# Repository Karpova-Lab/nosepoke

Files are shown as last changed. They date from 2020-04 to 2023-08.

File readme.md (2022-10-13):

# Nosepoke
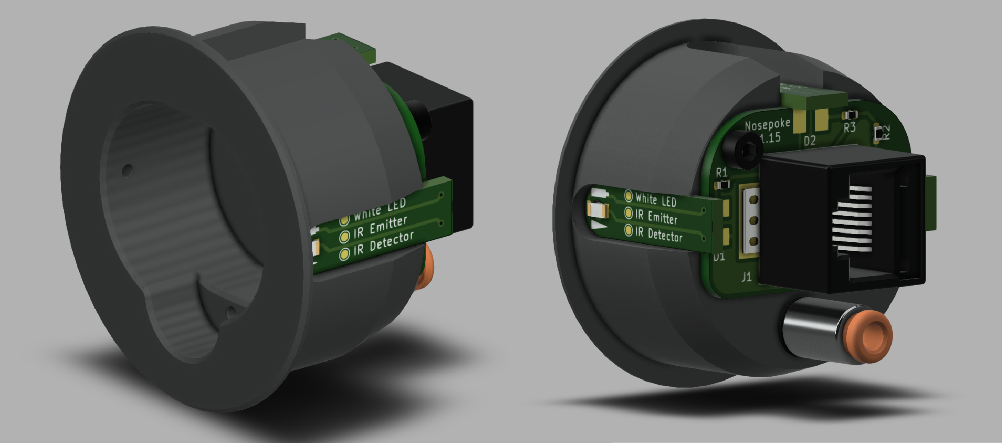
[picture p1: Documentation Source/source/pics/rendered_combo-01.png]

Full Documentation here: [https://karpova-lab.github.io/nosepoke/](https://karpova-lab.github.io/nosepoke/)

Ask questions here: [https://github.com/Karpova-Lab/nosepoke/discussions](https://github.com/Karpova-Lab/nosepoke/discussions)

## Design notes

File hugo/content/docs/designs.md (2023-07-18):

---
title: BOM and Design files
weight: 1
prev_txt: Overview
prev_link: ..
next_txt: Building
next_link: building
---

# Bill of Materials and Design Files

{{< pic file="parts.jpg" >}}

## Plastic Nosepoke Body

{{< columns >}}
{{< pic file="plastic.png" >}}
<--->

{{< pic file="nosepoke.png" >}}
{{< /columns >}}

{{< download filename="nosepoke.stl" text="nosepoke.stl" >}}
<br>
{{< download filename="nosepoke.step" text="nosepoke.step" >}}
<br>
{{< download filename="nosepoke_drawing.pdf" text="nosepoke_drawing.pdf" >}}

## PCBs and Electronics

PCB source files are on [GitHub](https://github.com/Karpova-Lab/nosepoke/tree/master/pcb)

{{< columns >}}

{{< pic file="back_pcb.png" >}}
{{< caption text="Rear PCB" >}}

<div style="text-align:center;">
<a href="https://oshpark.com/shared_projects/07c1qRaL">Order from OSH Park </a>
</div>
<--->

{{< pic file="outer_pcb.png" >}}

{{< caption text="Perimeter PCB" >}}

<div style="text-align:center;">
<a href="https://oshpark.com/shared_projects/ehOwH3Wp">Order from OSH Park </a>
</div>

{{< /columns >}}

| Qty | Reference | Description        | Value/MPN                                                                                                                                          |
| --- | --------- | ------------------ | -------------------------------------------------------------------------------------------------------------------------------------------------- |
| 1   | D1        | IR LED             | [IR26-21C/L110/TR8](https://www.digikey.com/products/en?keywords=1080-1357-1-ND)                                                                   |
| 1   | D2        | Diffused White LED | [23-11/T7D-CQ2R2QY/2A](https://www.digikey.com/products/en?keywords=1080-1593-1-ND)                                                                |
| 1   | J1        | RJ45 Jack          | [0855135013](https://www.digikey.com/products/en?keywords=WM3553CT-ND)                                                                             |
| 1   | Q1        | Phototransistor    | [PT26-21C/TR8](https://www.digikey.com/products/en?keywords=1080-1386-1-ND)                                                                        |
| 1   | R1        | 0603 Resistor      | [200Ω](https://www.digikey.com/en/products/detail/panasonic-electronic-components/ERJ-3EKF2000V/196205?s=N4IgTCBcDaIKICUBSBaAzHA0gMTABgIDUQBdAXyA) |
| 1   | R2        | 0603 Resistor      | [82Ω](https://www.digikey.com/products/en?keywords=311-82.0HRCT-ND)                                                                                |
| 1   | R3        | 0603 Resistor      | [10KΩ](https://www.digikey.com/en/products/detail/yageo/RC0603JR-0710KL/726700)                                                                    |
| 1   | R4        | 0603 Resistor      | [20KΩ](https://www.digikey.com/en/products/detail/yageo/RC0603JR-0720KL/726740)                                                                    |

{{< button href="ibom.html" >}}View interactive Bill of Materials{{< /button >}}

## Hardware
| QTY | Description                  | Part Number                                      | Supplier      |
| --- | ---------------------------- | ------------------------------------------------ | ------------- |
| 1   | 1/8" Push-to-connect fitting | [7880t137](https://www.mcmaster.com/7880t137)    | McMaster-Carr |
| 2   | 5mm long M2.5 x .45 screw    | [91290A100](https://www.mcmaster.com/91290A100/) | McMaster-Carr |

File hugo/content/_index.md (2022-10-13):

---
next_txt: BOMs and Design Files
next_link: designs
---
# Overview

<p>
    <a href="https://a360.co/349jTLC ">
        
    </a>
</p>
{{< caption text="Click to view CAD model" >}}

{{< pic file="exploded.png" >}}
{{< pic file="features.png" >}}

This is the documentation for building and using a nosepoke.
This project was developed in the [Karpova Lab](https://www.janelia.org/lab/karpova-lab) at HHMI's Janelia Research Campus for use in rodent behavioral experiments.

## Features

**Useful interface for rat**
  - Controllable overhead LED for lighting up the inside of the nosepoke
  - Infrared beam break for detecting nose insertion
  - Shelf for liquid reward to accumulate instead of dripping onto floor

**Easy installation and maintenance**
  - Designed to be press fit into 1.5" hole for easy installation and removal
  - Backside push-to-connect tube fitting for quick connection/disconnection when replacing liquid reward tubing

**Robust and manufacturable**
  - Designed to be machined out of hard plastic or aluminum by a typical machine shop. A less durable version could be 3D printed
  - Zero exposed wires, all connections are integrated into the PCB or made with solder joints. 
    - Removes possibility of connections coming loose or wires becoming damaged over time.
  - Electronics can be easily scaled to larger quantities
    - Single sided PCB with surface mount components is ideal for a PCB assembly service or manual assembly with a toaster oven/hot plate/heat gun.

**Open source**

  - All files are available on [GitHub](https://github.com/Karpova-Lab/nosepoke) and can be modified to meet custom needs

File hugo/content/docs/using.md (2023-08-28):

---
prev_txt: Building
prev_link: building
---
# Using

## pyControl

This nosepoke works with the [pyControl](https://pycontrol.readthedocs.io/en/latest/) behavior framework.
Specifically, this means that the RJ45 [pinout](https://pycontrol.readthedocs.io/en/latest/user-guide/hardware/#behaviour-ports) is compatible with pyControl.
Using an ethernet cable, you can connect the nosepoke to an [original breakout board](https://open-ephys.org/pycontrol/pycontrol) or a [D-series breakout board](https://karpova-lab.github.io/pyControl-D-Series-Breakout/index.html).

The latest software release can be downloaded [here](https://github.com/pyControl/code/releases).
Additional pyControl hardware can be purchased from the [Open Ephys Store](https://open-ephys.org/pycontrol).

## Example task

{{< hint info >}}

### <i class="fas fa-info-circle"></i> Note

For the example to work, this <a href="nosepoke.py" download > <i class="fa fa-download"></i> nosepoke.py </a> device file must be downloaded and placed in your `devices` folder.

{{< /hint >}}

Download <a href="nosepoke_example_task.py" download > <i class="fa fa-download"></i> nosepoke_example_task.py </a> and place it in your `tasks` folder.
This task assumes there is a nosepoke connected to **port 1** of the breakout board.

Instructions for using the pyControl GUI to upload and run a task can be found [here](https://pycontrol.readthedocs.io/en/latest/user-guide/graphical-user-interface/).

For more information on writing your own tasks, refer to the [pyControl documentation](https://pycontrol.readthedocs.io/en/latest/user-guide/programming-tasks/).

If you have questions, don't hesitate to post on the [nosepoke discussions board](https://github.com/Karpova-Lab/nosepoke/discussions).

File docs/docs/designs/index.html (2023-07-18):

Menu Table of Contents

# Bill of Materials and Design Files #

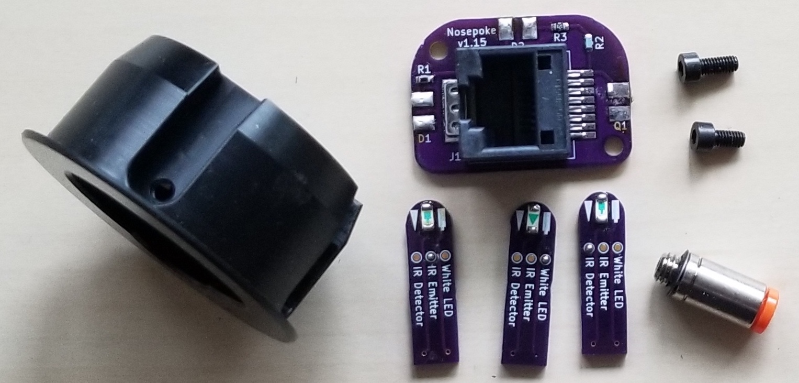
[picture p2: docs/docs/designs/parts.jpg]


## Plastic Nosepoke Body #

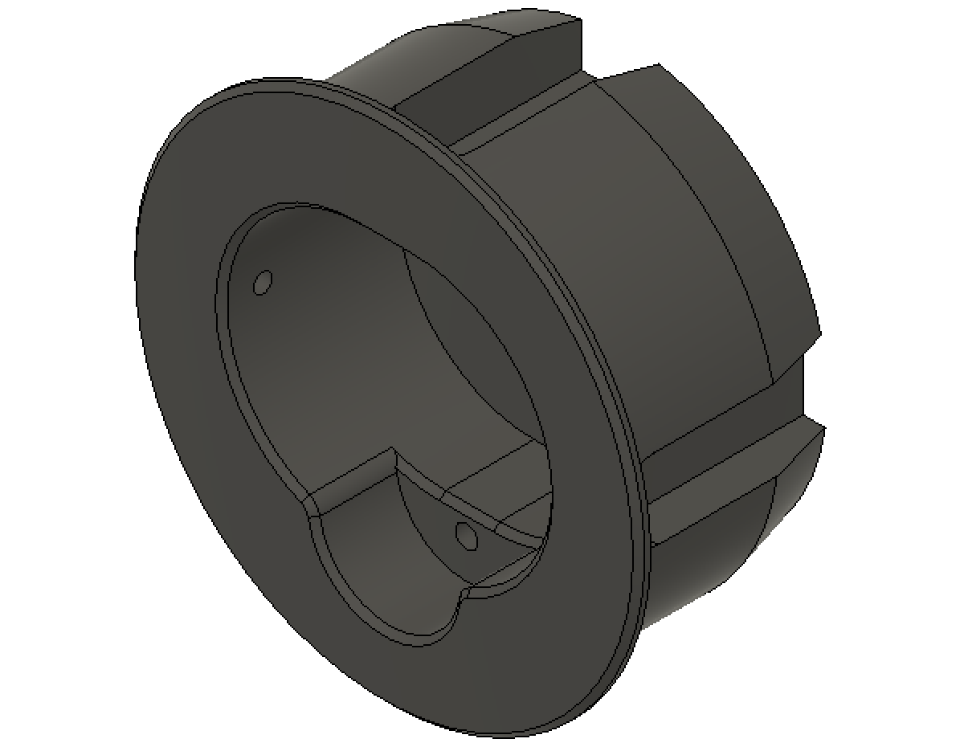
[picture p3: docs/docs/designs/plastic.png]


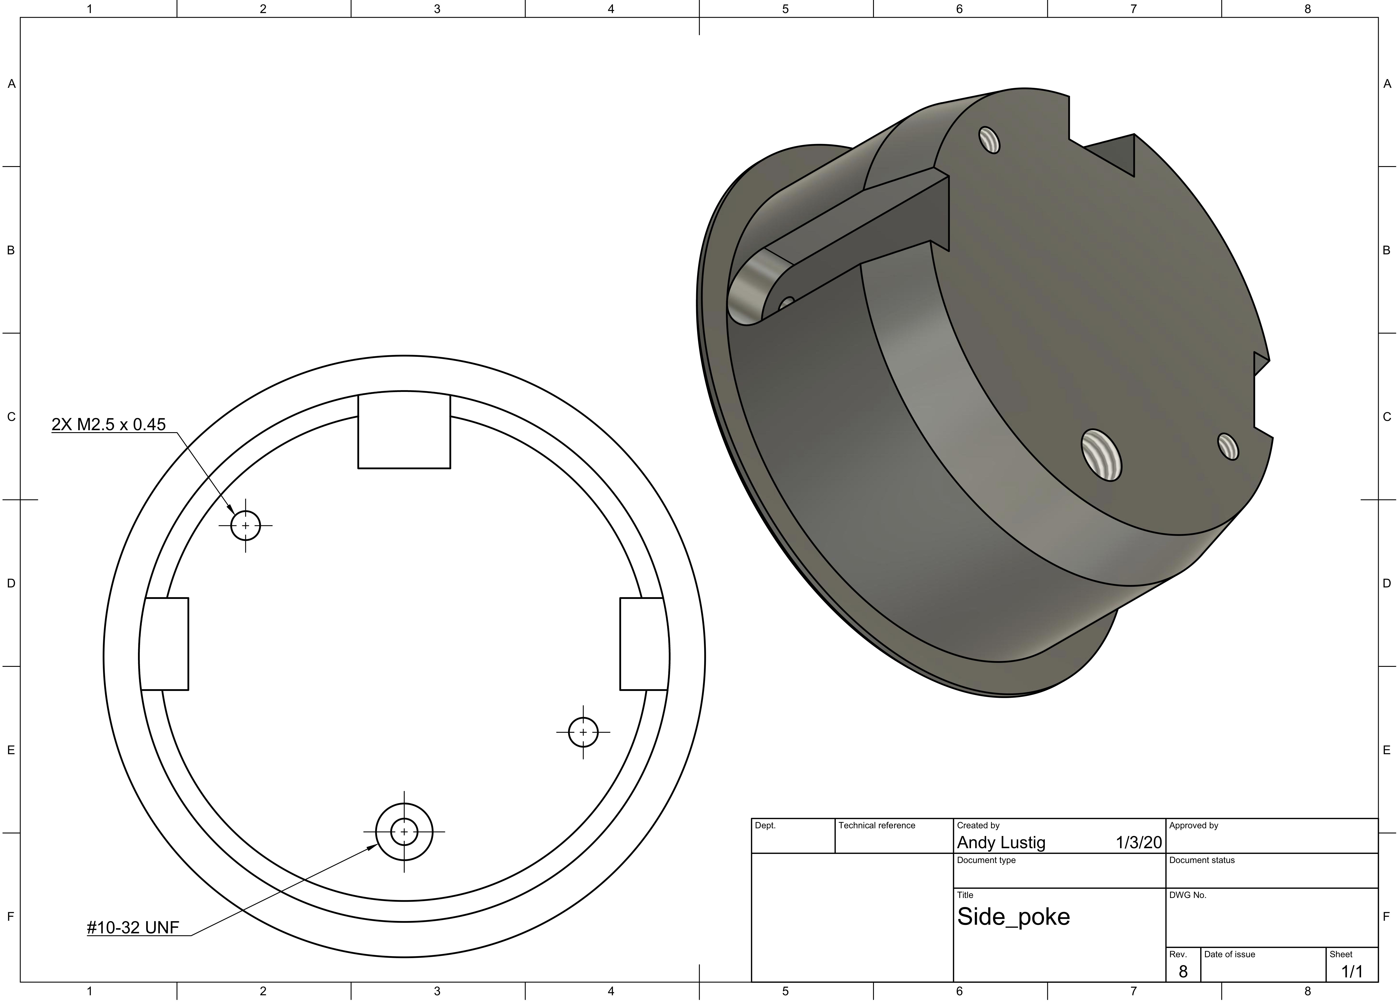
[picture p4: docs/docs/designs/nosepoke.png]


nosepoke.stl
nosepoke.step
nosepoke_drawing.pdf

## PCBs and Electronics #

PCB source files are on GitHub (https://github.com/Karpova-Lab/nosepoke/tree/master/pcb)

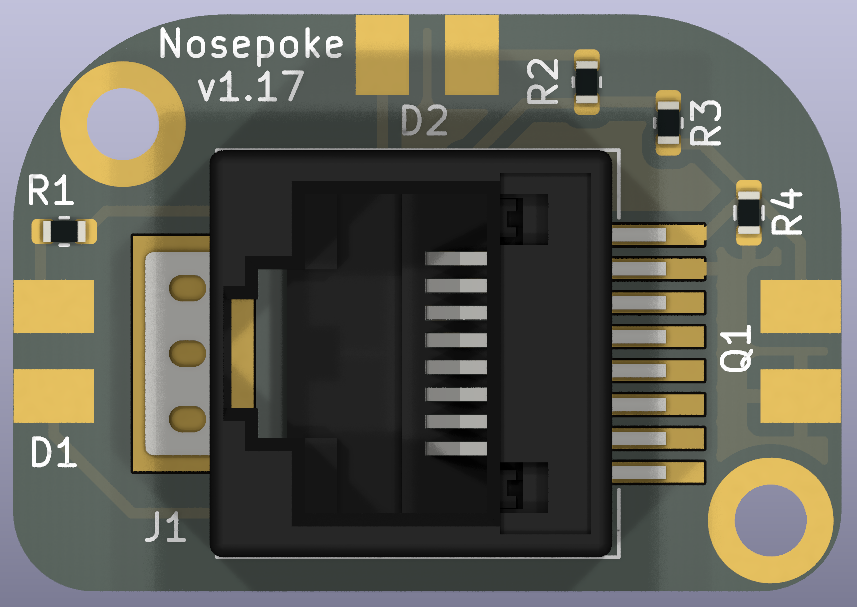
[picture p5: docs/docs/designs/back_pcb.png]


Rear PCB

Order from OSH Park (https://oshpark.com/shared_projects/07c1qRaL)

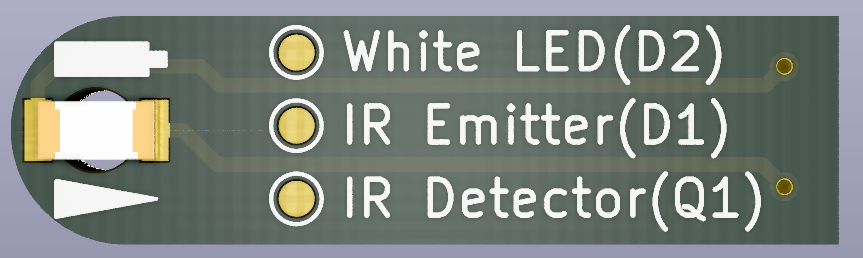
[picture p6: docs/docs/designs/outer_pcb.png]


Perimeter PCB

Order from OSH Park (https://oshpark.com/shared_projects/ehOwH3Wp)

Qty | Reference | Description | Value/MPN
1 | D1 | IR LED | IR26-21C/L110/TR8 (https://www.digikey.com/products/en?keywords=1080-1357-1-ND)
1 | D2 | Diffused White LED | 23-11/T7D-CQ2R2QY/2A (https://www.digikey.com/products/en?keywords=1080-1593-1-ND)
1 | J1 | RJ45 Jack | 0855135013 (https://www.digikey.com/products/en?keywords=WM3553CT-ND)
1 | Q1 | Phototransistor | PT26-21C/TR8 (https://www.digikey.com/products/en?keywords=1080-1386-1-ND)
1 | R1 | 0603 Resistor | 200Ω (https://www.digikey.com/en/products/detail/panasonic-electronic-components/ERJ-3EKF2000V/196205?s=N4IgTCBcDaIKICUBSBaAzHA0gMTABgIDUQBdAXyA)
1 | R2 | 0603 Resistor | 82Ω (https://www.digikey.com/products/en?keywords=311-82.0HRCT-ND)
1 | R3 | 0603 Resistor | 10KΩ (https://www.digikey.com/en/products/detail/yageo/RC0603JR-0710KL/726700)
1 | R4 | 0603 Resistor | 20KΩ (https://www.digikey.com/en/products/detail/yageo/RC0603JR-0720KL/726740)

View interactive Bill of Materials

## Hardware #

QTY | Description | Part Number | Supplier
1 | 1/8" Push-to-connect fitting | 7880t137 (https://www.mcmaster.com/7880t137) | McMaster-Carr
2 | 5mm long M2.5 x .45 screw | 91290A100 (https://www.mcmaster.com/91290A100/) | McMaster-Carr

previous
Overview (https://karpova-lab.github.io/nosepoke/) next
Building (https://karpova-lab.github.io/nosepoke/docs/building/)

These docs are built with Hugo (https://gohugo.io/). A forked version of Hugo Book (https://github.com/alustig3/hugo-book) is used as the theme.

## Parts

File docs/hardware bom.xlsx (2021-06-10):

QTY | Description | Part Number | Supplier | link | Price | Included QTY | Qty for # of pumps | Qty to order |  |  |  |  |  | 1 to 4 | for 5 | 10 to 49 | 50-99
1 | 1/8" Push-to-connect fitting | 7880t137 | McMaster-Carr | https://www.mcmaster.com/7880t137 | 2.81 | 1 | 1 | 1 | 2.81 | 1 Assemblies | $15.63 | $15.63 | .25" clear acylic | 86.9 | 36.94 | 31.56 | 30.22
2 | 5mm long M2.5 x .45 screw | 91290A100 | McMaster-Carr | https://www.mcmaster.com/91290A100/ | 12.82 | 50 | 2 | 1 | 12.82 |  |  |  | .249" aluminum 5052 | 105.3 | 49.22 | 45.29 | 42.15

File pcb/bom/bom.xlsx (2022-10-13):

Qty | Reference | Description | Value/MPN | Purchase Link
1 | D1 | IR LED | IR26-21C/L110/TR8 | https://www.digikey.com/products/en?keywords=1080-1357-1-ND
1 | D2 | Diffused White LED | 23-11/T7D-CQ2R2QY/2A | https://www.digikey.com/products/en?keywords=1080-1593-1-ND
1 | J1 | RJ45 Jack | 0855135013 | https://www.digikey.com/products/en?keywords=WM3553CT-ND
1 | Q1 | Phototransistor | PT26-21C/TR8 | https://www.digikey.com/products/en?keywords=1080-1386-1-ND
1 | R1 | 0603 Resistor | 200Ω | https://www.digikey.com/products/en?keywords=P330HCT-ND
1 | R2 | 0603 Resistor | 82Ω | https://www.digikey.com/products/en?keywords=311-82.0HRCT-ND
1 | R3 | 0603 Resistor | 10KΩ | https://www.digikey.com/product-detail/en/RC0603JR-0710KL/311-10KGRCT-ND/729647/?itemSeq=322900504
1 | R4 | 0603 Resistor | 20KΩ | https://www.digikey.com/product-detail/en/RC0603JR-0710KL/311-10KGRCT-ND/729647/?itemSeq=322900504

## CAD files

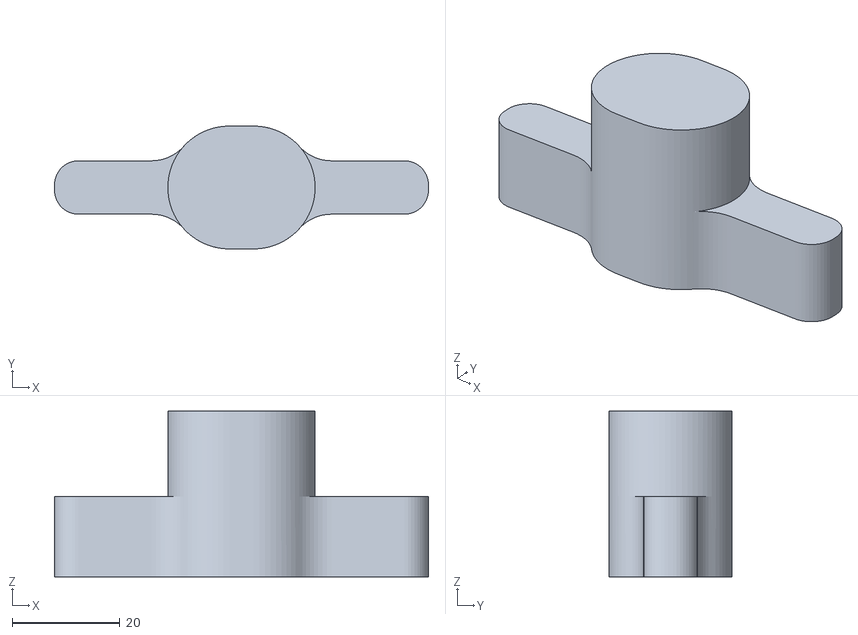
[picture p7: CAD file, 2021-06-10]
3d CAD/nosepoke_aligner.stl
69.3 x 22.8 x 30.7

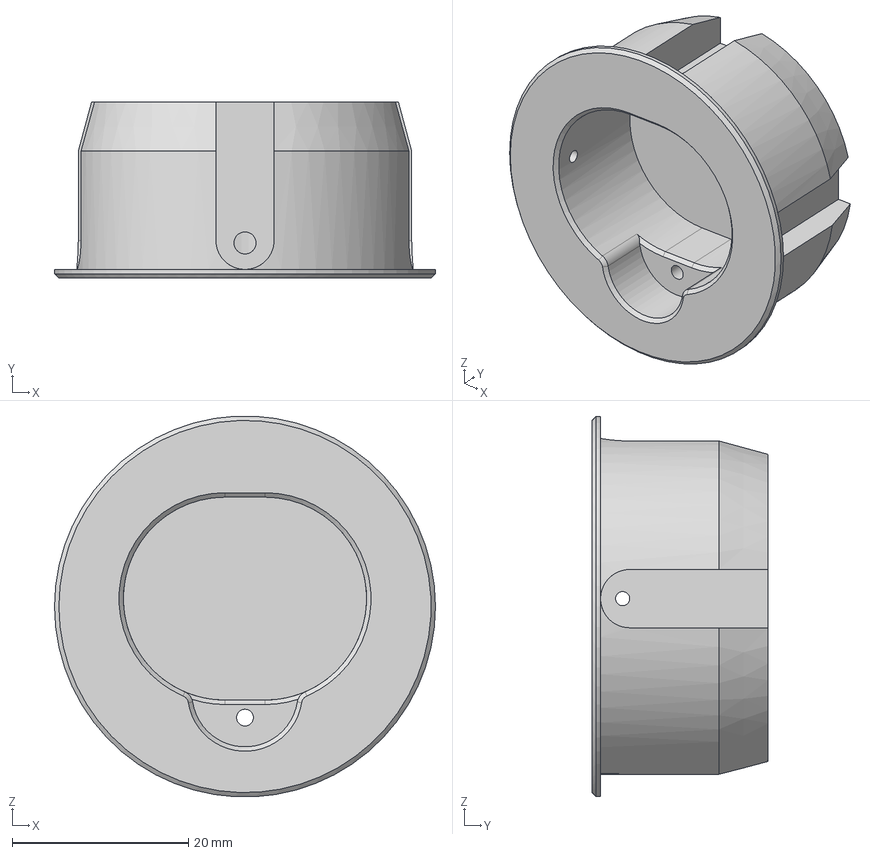
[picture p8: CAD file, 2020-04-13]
docs/docs/designs/nosepoke.step
43.2 x 20.0 x 43.1 mm

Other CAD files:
docs/docs/designs/nosepoke.stl
hugo/content/docs/designs/nosepoke.stl

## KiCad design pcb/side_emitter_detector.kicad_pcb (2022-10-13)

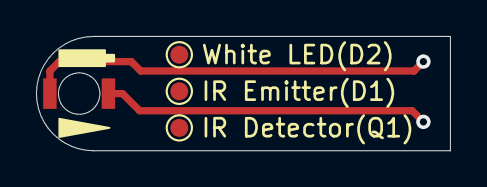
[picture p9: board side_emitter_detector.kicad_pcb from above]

Board: 2 copper layers, 23.0 x 6.4 mm, 5 parts (1 on the bottom side), 2 nets.

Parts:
D1: LED; 1206_reverse_smd
IR Detector(Q1): TestPoint; TestPoint_Pad_D1.0mm
IR Emitter(D1): TestPoint; TestPoint_Pad_D1.0mm
J1: Conn_01x02_Male; board_to_board_joint
White LED(D2): TestPoint; TestPoint_Pad_D1.0mm

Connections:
unnamed: D1.1, J1.2
unnamed: D1.2, J1.1

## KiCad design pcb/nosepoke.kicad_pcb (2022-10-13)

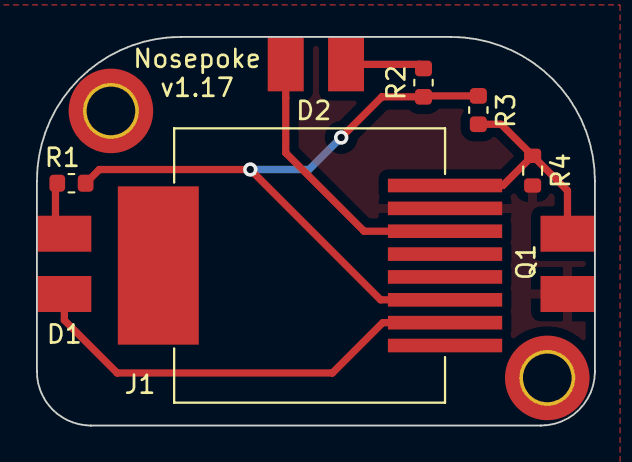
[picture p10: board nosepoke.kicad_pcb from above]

Board: 2 copper layers, 31.0 x 21.6 mm, 10 parts (0 on the bottom side), 7 nets.

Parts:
D1: IR26-21C/L110/TR8; board_to_board_joint
D2: 23-11/T7D-CQ2R2QY/2A; board_to_board_joint
H1, H2: MountingHole; MountingHole_2.7mm_M2.5_DIN965_Pad_TopOnly
J1: 0855135013; RJ45_SMD_Vertical
Q1: PT26-21C/TR8; board_to_board_joint
R1: 200Ω; R_0603_1608Metric
R2: 82Ω; R_0603_1608Metric
R3: 10KΩ; R_0603_1608Metric
R4: 20KΩ; R_0603_1608Metric

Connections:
+5V: J1.6 (5V), R1.2, R2.2, R3.2
/DIO_A: J1.1 (DIO-A), Q1.1 (C), R3.1, R4.2
GND: J1.2 (GND), Q1.2 (E), R4.1
unnamed: D1.1 (K), J1.7 (POW-B)
unnamed: D1.2 (A), R1.1
unnamed: D2.1 (K), J1.3 (POW-A)
unnamed: D2.2 (A), R2.1

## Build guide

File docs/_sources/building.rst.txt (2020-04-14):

:github_url: https://github.com/Karpova-Lab/nosepoke

.. include:: isogrk1.txt

Building
--------
.. image:: pics/parts.jpg
  :align: center

Components
++++++++++
  
Plastic Nosepoke Body
=====================
.. image:: pics/plastic.png
  :width: 39%

.. image:: pics/nosepoke.png
  :target: _static/nosepoke.pdf
  :width: 59%

- Download :download:`nosepoke.stl <_static/nosepoke.stl>` 
- Download :download:`nosepoke.step <_static/nosepoke.step>` 

PCBs and Electronics
====================
PCB source files are on `GitHub <https://github.com/Karpova-Lab/nosepoke/tree/master/pcb>`_ 

.. image:: pics/back_pcb.png
  :width: 60%

.. raw:: html

  <a href="https://oshpark.com/shared_projects/PgBzF9ZE">
      
  </a></div>

.. image:: pics/outer_pcb.png
  :width: 60%

.. raw:: html

  <a href="https://oshpark.com/shared_projects/ehOwH3Wp">
      
  </a>

+-----+-----------+--------------------+--------------------------------------------------------------------------------------------------------------+
| Qty | Reference | Description        | Value/MPN                                                                                                    | 
+=====+===========+====================+==============================================================================================================+
| 1   | D1        | IR LED             | `IR26-21C/L110/TR8 <https://www.digikey.com/products/en?keywords=1080-1357-1-ND>`_                           | 
+-----+-----------+--------------------+--------------------------------------------------------------------------------------------------------------+
| 1   | D2        | Diffused White LED | `23-11/T7D-CQ2R2QY/2A <https://www.digikey.com/products/en?keywords=1080-1593-1-ND>`_                        | 
+-----+-----------+--------------------+--------------------------------------------------------------------------------------------------------------+
| 1   | J1        | RJ45 Jack          | `0855135013 <https://www.digikey.com/products/en?keywords=WM3553CT-ND>`_                                     | 
+-----+-----------+--------------------+--------------------------------------------------------------------------------------------------------------+
| 1   | Q1        | Phototransistor    | `PT26-21C/TR8 <https://www.digikey.com/products/en?keywords=1080-1386-1-ND>`_                                | 
+-----+-----------+--------------------+--------------------------------------------------------------------------------------------------------------+
| 1   | R1        | 0603 Resistor      | `330Ω <https://www.digikey.com/products/en?keywords=P330HCT-ND>`_                                            | 
+-----+-----------+--------------------+--------------------------------------------------------------------------------------------------------------+
| 1   | R2        | 0603 Resistor      | `10KΩ <https://www.digikey.com/product-detail/en/RC0603JR-0710KL/311-10KGRCT-ND/729647/?itemSeq=322900504>`_ | 
+-----+-----------+--------------------+--------------------------------------------------------------------------------------------------------------+
| 1   | R3        | 0603 Resistor      | `82Ω <https://www.digikey.com/products/en?keywords=311-82.0HRCT-ND>`_                                        | 
+-----+-----------+--------------------+--------------------------------------------------------------------------------------------------------------+

.. raw:: html

  <div style="text-align:center; margin-bottom:24px">
    <a href="_static/backside_ibom.html" style="background-color: #2980b9;
    border: none;
    color: white;
    padding: 15px 15px;
    text-align:center;
    text-decoration: none;
    display: inline-block;
    font-size: 18px;
    border-radius:15px">View interactive BOM</a>
  </div>

Hardware
========
+-----+--------------------------------+--------------------------------------------------------------------------------+---------------+
| Qty | Description                    | Part Number                                                                    | Supplier      | 
+=====+================================+================================================================================+===============+
| 1   | 1/8" Push-to-connect fitting   | `7880t137 <https://www.mcmaster.com/7880t137>`_                                | McMaster-Carr | 
+-----+--------------------------------+--------------------------------------------------------------------------------+               +
| 2   | 5mm long M2.5 x .45 screw      | `91290A100 <https://www.mcmaster.com/91290a100>`_                              |               | 
+-----+--------------------------------+--------------------------------------------------------------------------------+---------------+

Assembly
++++++++

Required Tools
==============
- 2mm hex key or  `screwdriver <https://www.mcmaster.com/57585a53>`_ 
- Soldering iron 

Instructions
============
#. Solder components onto backside PCB.
#. Secure backside PCB to the back of the nosepoke using two M2.5 screws.
#. Solder components onto the perimeter PCBs.
#. Place the perimeter PCBs into the channels of the nosepoke. The IR emitter (D1) goes on the left side, the white LED (D2) goes on top and the phototransistor (Q1) goes on the right side.
#. Add solder to the joints of the PCBs to create both electrical and mechanical connections.
#. Using a 2mm hex key or screwdriver, screw in the push-to-connect fitting.

.. image:: pics/solid_color.gif
  :align: center
  
.. image:: pics/wireframe.gif
  :align: center

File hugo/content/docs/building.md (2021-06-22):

---
prev_txt: BOM and Design Files
prev_link: designs
next_txt: Using
next_link: using
---
# Building


## Required Tools
- 2mm hex key or [screwdriver](https://www.mcmaster.com/57585a53)  
- Soldering iron 

## Instructions
1. Secure backside PCB to the back of the nosepoke using two M2.5 screws.

{{< columns >}}

{{< pic file="backside_before.jpg" >}}

<--->

{{< pic file="backside_after.jpg" >}}
{{< /columns >}}

2. Place the perimeter PCBs into the channels of the nosepoke and solder the joints of the PCBs to create both electrical and mechanical connections.

{{< hint info >}}
### <i class="fas fa-info-circle"></i> Note
The IR emitter (D1) goes on the left side, the white LED (D2) goes on top and the phototransistor (Q1) goes on the right side.

{{< /hint >}}

{{< pic file="perimeter_before.jpg" >}}

{{< columns >}}
{{< pic file="adding_joint.jpg" >}}
<--->

{{< pic file="final_joints.jpg" >}}
{{< /columns >}}

3. Using a 2mm hex key or screwdriver, screw in the push-to-connect fitting.

{{< columns >}}
{{< pic file="pushconnect_before.jpg" >}}
<--->
{{< pic file="pushconnect_after.jpg" >}}

{{< /columns >}}

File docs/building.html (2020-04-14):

- Docs »
- Building
- View GitHub Repo (https://github.com/Karpova-Lab/nosepoke)

Next Previous

# Building¶



## Components¶

### Plastic Nosepoke Body¶

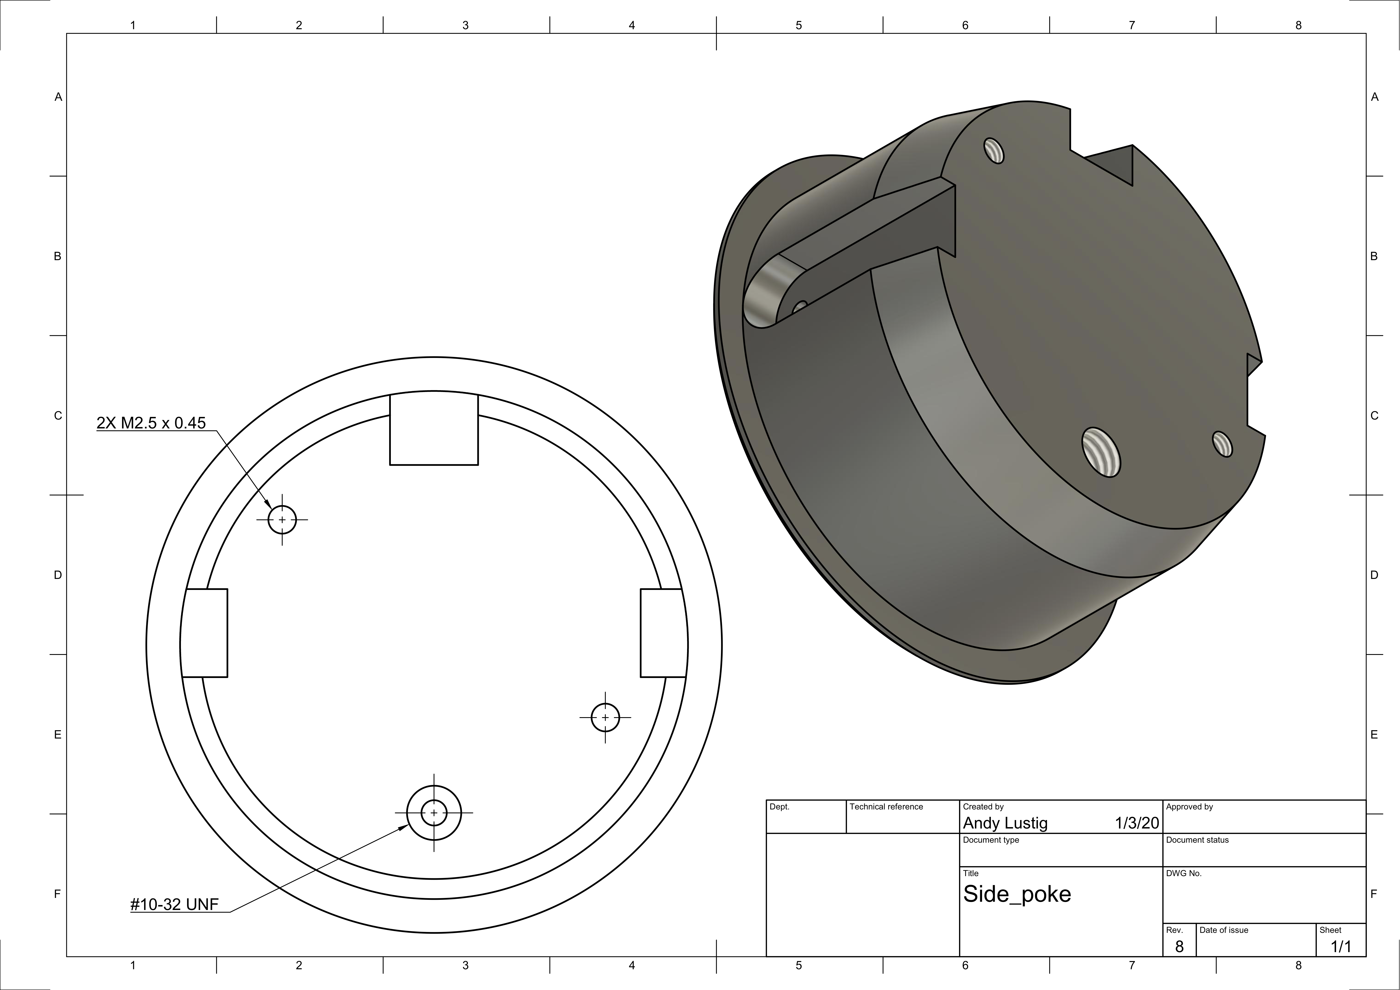
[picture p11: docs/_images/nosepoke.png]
 

- Download nosepoke.stl
- Download nosepoke.step

### PCBs and Electronics¶

PCB source files are on GitHub (https://github.com/Karpova-Lab/nosepoke/tree/master/pcb)

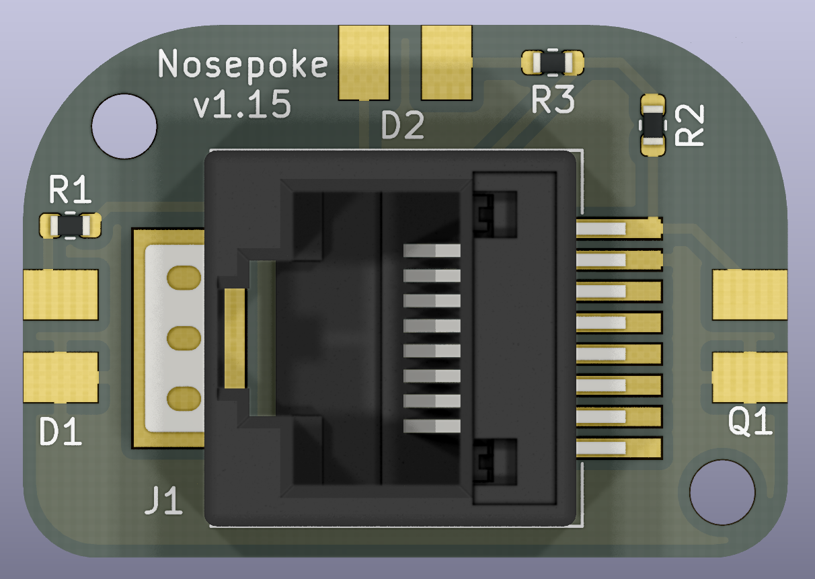
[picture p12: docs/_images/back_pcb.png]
  (https://oshpark.com/shared_projects/PgBzF9ZE)

  (https://oshpark.com/shared_projects/ehOwH3Wp)

Qty | Reference | Description | Value/MPN
1 | D1 | IR LED | IR26-21C/L110/TR8 (https://www.digikey.com/products/en?keywords=1080-1357-1-ND)
1 | D2 | Diffused White LED | 23-11/T7D-CQ2R2QY/2A (https://www.digikey.com/products/en?keywords=1080-1593-1-ND)
1 | J1 | RJ45 Jack | 0855135013 (https://www.digikey.com/products/en?keywords=WM3553CT-ND)
1 | Q1 | Phototransistor | PT26-21C/TR8 (https://www.digikey.com/products/en?keywords=1080-1386-1-ND)
1 | R1 | 0603 Resistor | 330Ω (https://www.digikey.com/products/en?keywords=P330HCT-ND)
1 | R2 | 0603 Resistor | 10KΩ (https://www.digikey.com/product-detail/en/RC0603JR-0710KL/311-10KGRCT-ND/729647/?itemSeq=322900504)
1 | R3 | 0603 Resistor | 82Ω (https://www.digikey.com/products/en?keywords=311-82.0HRCT-ND)

View interactive BOM

### Hardware¶

Qty | Description | Part Number | Supplier
1 | 1/8” Push-to-connect fitting | 7880t137 (https://www.mcmaster.com/7880t137) | McMaster-Carr
2 | 5mm long M2.5 x .45 screw | 91290A100 (https://www.mcmaster.com/91290a100)

## Assembly¶

### Required Tools¶

- 2mm hex key or screwdriver (https://www.mcmaster.com/57585a53)
- Soldering iron

### Instructions¶

1. Solder components onto backside PCB.
2. Secure backside PCB to the back of the nosepoke using two M2.5 screws.
3. Solder components onto the perimeter PCBs.
4. Place the perimeter PCBs into the channels of the nosepoke. The IR emitter (D1) goes on the left side, the white LED (D2) goes on top and the phototransistor (Q1) goes on the right side.
5. Add solder to the joints of the PCBs to create both electrical and mechanical connections.
6. Using a 2mm hex key or screwdriver, screw in the push-to-connect fitting.

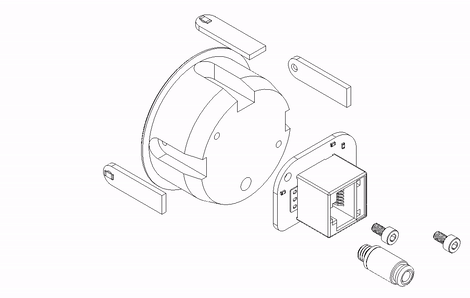
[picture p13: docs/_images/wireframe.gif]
 

Next Previous

© Copyright 2018-2019, Andy Lustig Last updated on Apr 14, 2020.

Built with Sphinx (http://sphinx-doc.org/) using a theme (https://github.com/rtfd/sphinx_rtd_theme) provided by Read the Docs (https://readthedocs.org).

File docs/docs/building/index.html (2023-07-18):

Menu Table of Contents

# Building #



## Required Tools #

- 2mm hex key or screwdriver (https://www.mcmaster.com/57585a53)
- Soldering iron

## Instructions #

1. Secure backside PCB to the back of the nosepoke using two M2.5 screws.

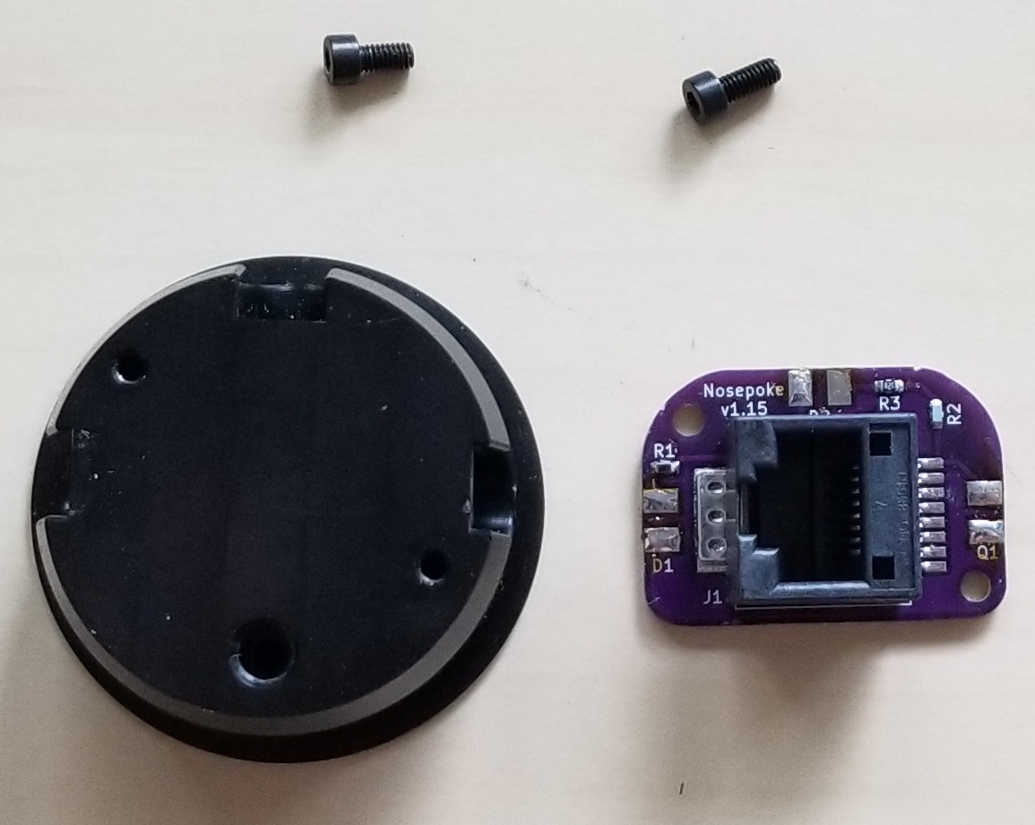
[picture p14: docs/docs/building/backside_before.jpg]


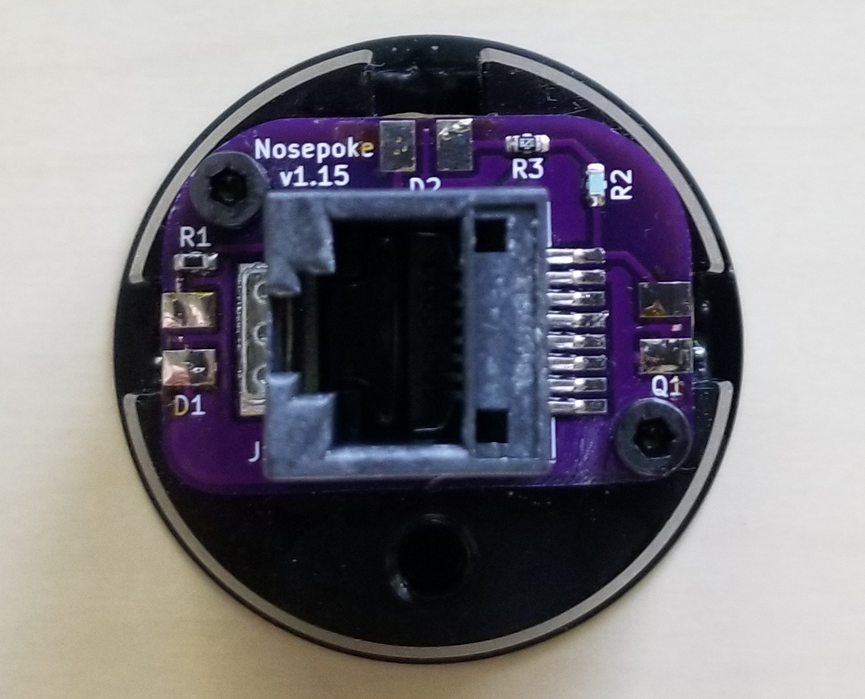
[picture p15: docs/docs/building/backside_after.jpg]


2. Place the perimeter PCBs into the channels of the nosepoke and solder the joints of the PCBs to create both electrical and mechanical connections.

### Note #

The IR emitter (D1) goes on the left side, the white LED (D2) goes on top and the phototransistor (Q1) goes on the right side.

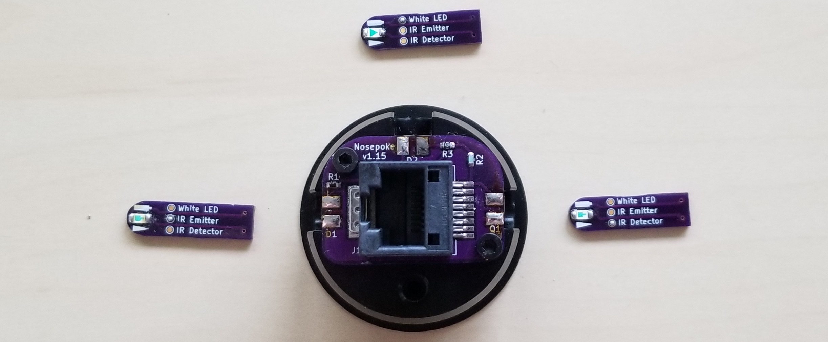
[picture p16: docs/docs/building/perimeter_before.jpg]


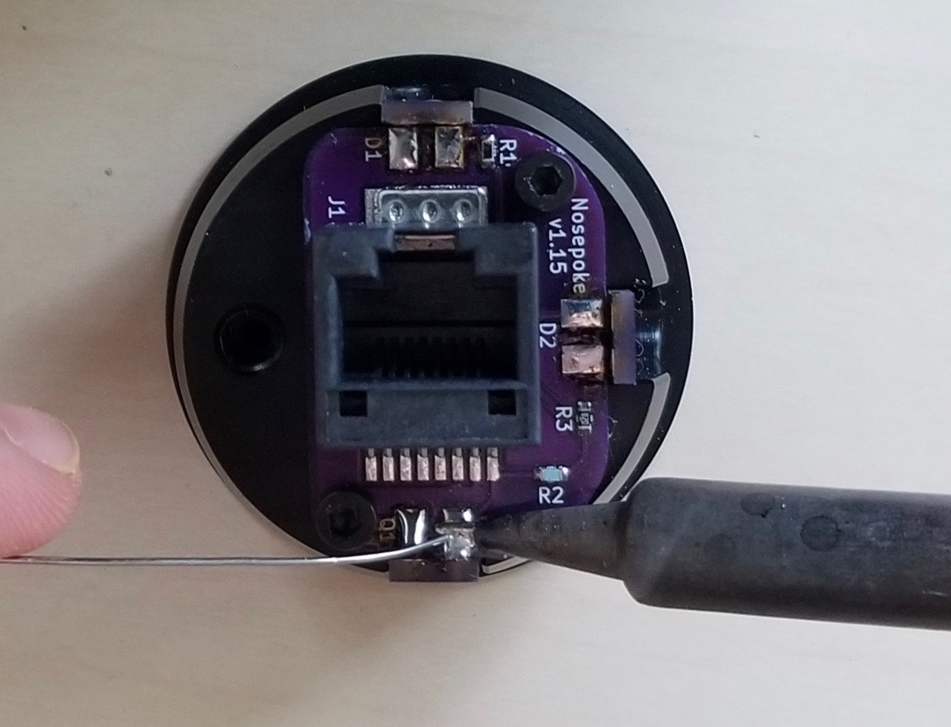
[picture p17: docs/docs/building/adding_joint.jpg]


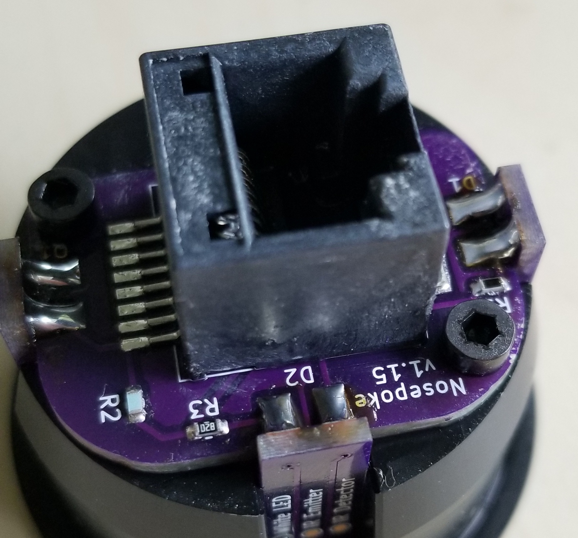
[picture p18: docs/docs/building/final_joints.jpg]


3. Using a 2mm hex key or screwdriver, screw in the push-to-connect fitting.

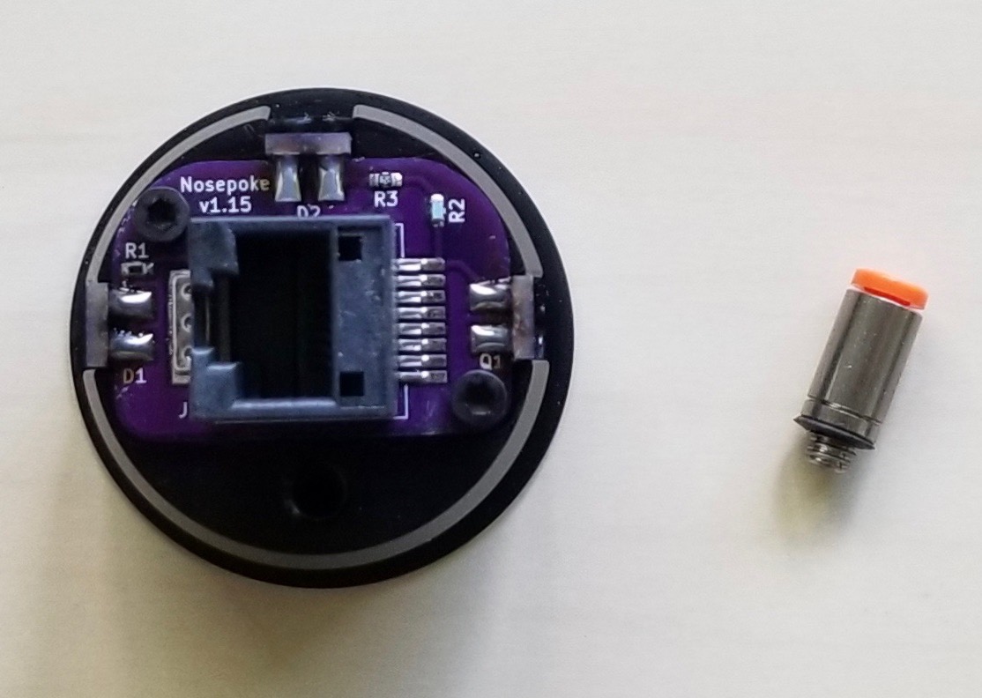
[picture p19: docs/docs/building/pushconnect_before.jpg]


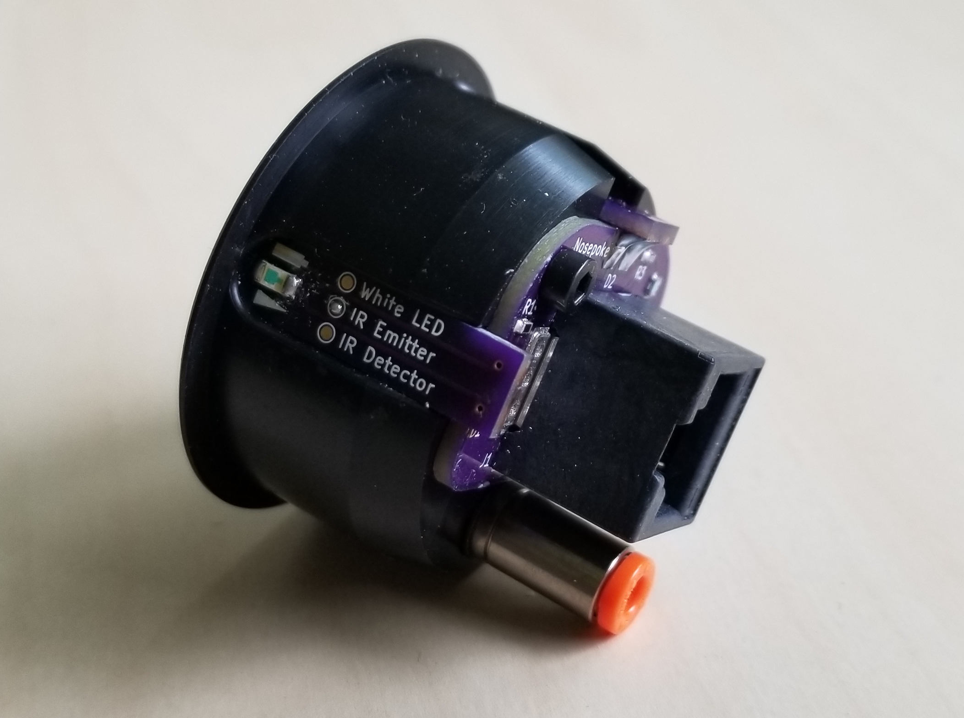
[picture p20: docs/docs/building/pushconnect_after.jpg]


previous
BOM and Design Files (https://karpova-lab.github.io/nosepoke/docs/designs/) next
Using (https://karpova-lab.github.io/nosepoke/docs/using/)

These docs are built with Hugo (https://gohugo.io/). A forked version of Hugo Book (https://github.com/alustig3/hugo-book) is used as the theme.

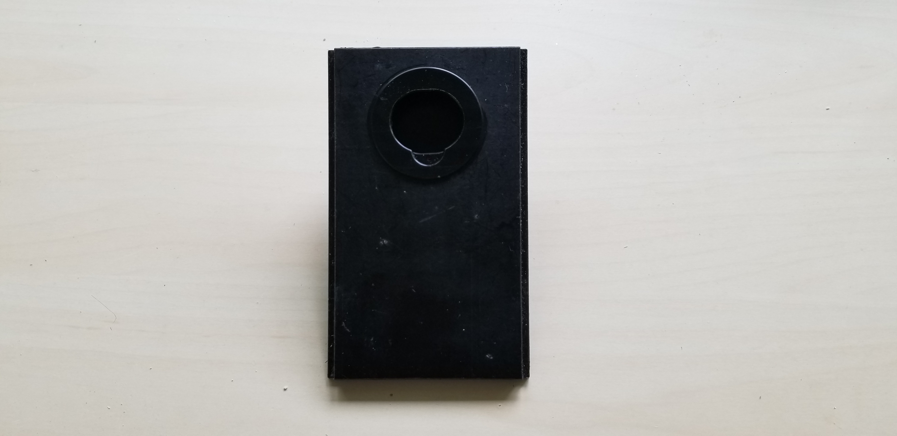
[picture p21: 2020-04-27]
hugo/content/docs/building/press_after_2.jpg

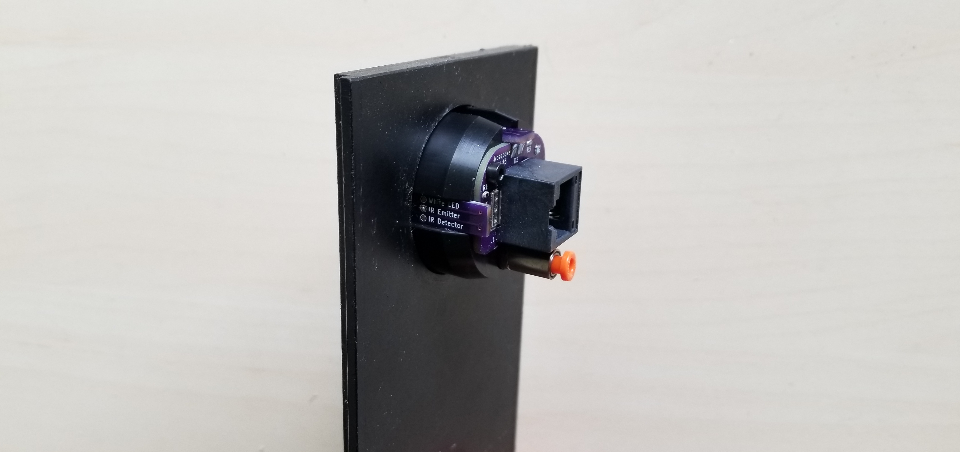
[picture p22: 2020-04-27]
docs/docs/building/press_after_1.jpg

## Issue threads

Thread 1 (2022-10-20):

### ISSUE TITLE
Resistors for V1.15 and solidworks file

### ISSUE THREAD

**Issue by thomasrgray** [Karpova-Lab/nosepoke#1]
Hello,

I was wondering if you can post the parts list for the V1.15 version and the solidworks file for the nosepoke body?

**Comment by alustig3** [comment]
Hi,

I don't have a Solidworks file specifically, but a step file, which you should be able to open with Solidworks, can be found [here](https://karpova-lab.github.io/nosepoke/docs/designs/#plastic-nosepoke-body).

I recommend using [PCB v1.17](https://oshpark.com/shared_projects/07c1qRaL) (sorry the [link in the documentation](https://karpova-lab.github.io/nosepoke/docs/designs/#pcbs-and-electronics) is out of date, I will update it soon). The main difference between v1.17 and v1.15 is that the IR emitter LED can now be turned off when not being used, which greatly extends the life of the LED. A BOM for PCB, including resistors, can be found [here(interactive)](https://karpova-lab.github.io/nosepoke/docs/designs/ibom.html) and [here(w/purchase links)](https://karpova-lab.github.io/nosepoke/docs/designs/#pcbs-and-electronics). 

I hope that answers your questions. Don't hesitate to reach out if you have more!

**Comment by alustig3** [comment]
Documentation has been updated with links and images for PCB v1.17 1b5cfa0ab71ac33a03055e42cff861d6122487c5

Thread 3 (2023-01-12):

### ISSUE TITLE
IR sensor phototransistor is sensitive to visible light

### ISSUE THREAD

**Issue by danielsvedberg** [Karpova-Lab/nosepoke#3]
[The karpova lab BOM](https://karpova-lab.github.io/nosepoke/docs/designs/) lists[PT26-21C/TR8](https://www.digikey.com/products/en?keywords=1080-1386-1-ND) as the specified phototransistor. The [phototransistor documents](https://media.digikey.com/pdf/Data%20Sheets/Everlight%20PDFs/PT26-21C_TR8.pdf) indicate that "The device is Spectrally matched to visible and infrared emitting diode". This means that any ambient light, such as the nosepoke's own white-light LED, may potentially trigger the phototransistor. Typically, IR sensors spec photodiodes/transistors with a dark lens to prevent visible light from triggering the sensor. Is this an issue you have observed / is a visible-light sensitive phototransistor the correct spec, or is there an error?

**Comment by alustig3** [comment]
Thanks for the question. This has not been an issue for us.

When there is nothing in the nosepoke, the phototransistor is already saturated with light from the IR emitter, so adding or removing other light will have no effect.

The irradiance required to get the current flowing well through the phototransitor is actually pretty high. In this case, we achieve it by having a well aligned IR emitter (close to the photransistor's peak spectral sensitivity) shining directly into it (at its peak angular sensitivity). When something is inside the nosepoke and disrupts the light coming from the IR emitter, the decrease in irradiance is drastic. It would be extremely difficult for other light sources to reach the phototransistor with enough power to replace the light that was being shined into the photoransistor by the IR emitter under ideal conditions.

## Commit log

2019-01-17 Doc update
    [hardware bom.xlsx]
2020-04-13 Update to pyControl compatible nosepoke. Plastic body is shorter. No longer have lick detection. New shorter PCBs, designed in KiCAD. Big documentation update.
    [Nose IR emitter 1.2.brd, Nose IR emitter 1.2.sch, Side_poke v19.step, Side_poke v19.stl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]
2020-04-14 fix doc pcb images
2020-04-27 Improved assembly instructions with pictures.
    [nosepoke.step, nosepoke.stl]
2021-03-17 rear pcb v1.16
    [bom.xlsx, nosepoke.kicad_pcb, nosepoke.kicad_sch, nosepoke.sch]
2021-06-03 transition to hugo
    [hardware bom.xlsx, nosepoke.step, nosepoke.stl]
2021-06-03 added nosepoke aligner
    [insert.dxf, nosepoke_aligner.stl]
2021-06-22 rearranged docs. added BOM and design files section
    [nosepoke.step, nosepoke.stl]
2021-06-22 fixed broken assembly image links
2022-10-13 backside PCB v1.17
    [bom.xlsx, nosepoke.kicad_pcb, nosepoke.kicad_sch, side_emitter_detector.kicad_pcb]
2022-10-13 doc updates for PCB v1.17
2023-01-12 updated hugo theme submodule
    [nosepoke.kicad_sch]
2023-01-12 R1 link in docs now points to a 200Ω resistor on digikey
    fixes https://github.com/Karpova-Lab/nosepoke/issues/2
